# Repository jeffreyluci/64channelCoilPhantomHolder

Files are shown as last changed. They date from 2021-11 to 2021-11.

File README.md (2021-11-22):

# 64 Channel Coil Phantom Holder for FUNSTAR Phantom
Development resources for creating a [FUNSTAR](https://www.goldstandardphantoms.com/products/funstar/) phantom holder for a Siemens 64 channel Head/Neck coil

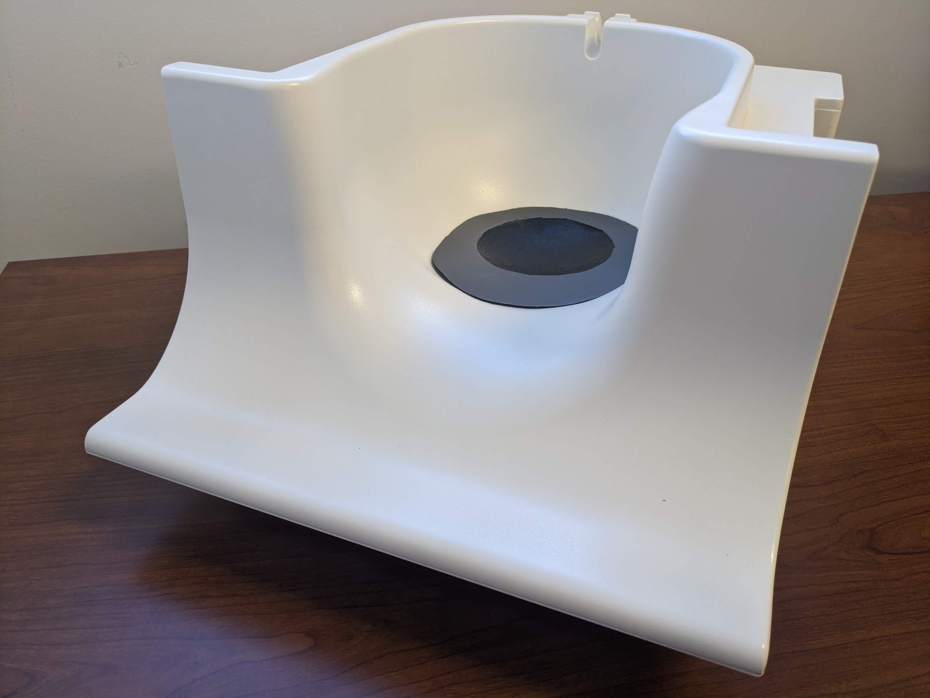
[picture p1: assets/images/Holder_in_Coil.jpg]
Phantom holder in Siemens 64 channel head coil


The analysis I perform for QA monitors individual coil elements, and the phantom's position in the coil affects loading and sensitivities of all the elements. Placing the phantom reproducibly within the coil housing enables more rigorous monitoring and comparison of long-term metrics. To that end, I have used CAD files of the coil housings to create my custom phantom holders. Unfortunately, having just moved to Rutgers University and switching to a Prisma, my primary coil for QA is now the 64 channel head/neck. Previously, I had used the 32 head. Snice I don't have, and didn't want to wait for the (approximately) 284 lawyers it takes to obtain the CAD files for this coil, I acquired a high resolution CT of the coil housing, and modeled the surface in [Autodesk Inventor.](https://www.autodesk.com/products/inventor/overview) From that, I created a holder that meshes with the surface of the coil, and has a shperoid cutout that matches the FUNSTAR outer diameter.

A few caveats. This phantom holder is in direct contact with the coil housing and does not provide any effective vibration mitigation measures. I am still trying to rigorously characterize the mechanical vibrations, and how much they affect the results of QA (if at all). I am also trying to get the CAD files for the 64 channel head/neck coil. If/when I am able to do that, I will create a revised version of this holder and update this posting.

I 3D printed the holder on an FDM printer using ABS as the filament material. My plan was to use this print as a prototype to see if my modeled coil surface needed any significant tweaks to resolve mismatched features. Once those tweaks were made, I would reprint the holder using a SLA or SLS printer. While placement of the center of the phantom ended up off center by about 2 mm, I was very pleased with the surface matching, and decided that I didn't need to improve upon the design or material.

The coil was printed with the flat surface down. That left the phantom mating depression quite rough from lack of enough supports. However, using a [Dremmel tool](https://us.dremel.com/en_US/products/-/show-product/tools/4300-high-performance-variable-speed-rotary-tool) on medium speed fitted with a [Dremel 414 polishing wheel](https://us.dremel.com/en_US/products/-/show-product/accessories/dremel-414-felt-polishing-wheel) cleaned it up very nicely. That process took only a few minutes. I recommend wearing a mask for this part of the process to prevent inhaling any ABS dust. I sure hope you can find a facemask somewhere. 

I coated the coil and phantom mating surfaces with (please don't laugh) [black Flex Seal spray.](https://flexsealproducts.com/products/flex-seal) (I figured if it's good enough to float a fishing boat . . .) I used 8 coats for the coil mating surface, and 5 coats for the phantom side. The rubberized surface provides excellent grip to prevent sliding, yet leaves no sticky residue or discoloration of the coil or phantom. I plan on peeling off the Flex Seal coating to reapply when/if it becomes brittle or loses its grippy properties. It peels off easily from the ABS, but it adheres strong enough that I'm not overly concerned about durability under normal use.

I have attached a zip file with photos of the holder after printing at various stages of finishing. I chose to mask off the flat surface of the holder, but if I had it to do over again, I wouldn't do that. It was unnecessary, and I probably reduced the lifetime of the rubber by creating "sharp" edges where the rubber could peel. The photos of the holder in the coil are a little misleading. The rubber intentionally curls up just a bit around the surface, and that makes it look as though there is a shadow indicating a gap between the holder and the coil surface. There isn't one. It's a very tight fit.

I have also attached STL files. One at "low" resolution for FDM printers, and one at "high" resolution for SLA or SLS printers. I used the FDM printer version, and its "smoothness" is more than adequate after rubberization. 

Finally, I have attached the AutoCAD Inventor model I created that subsequently produced the STL files. DM for my Venmo for gratuities!

I hope these help you, and if you have questions or need help using these resources, feel free to contact me. I'm always happy to help and collaborate.

## LICENSE and TERMS OF USE

All information contained in this repository is copyrighted by Jeffrey Luci, 2021. Jeffrey Luci grants non-exclusive, revocable license to use the information contained in this repository to all persons for non-commercial use, provided that works using information in this respository (including those that build upon, modify, or improve the design) in publication or presentation must reference this repository formally, in accordance with the accepted practices, procedures, and styles of the relevant publishing entity. **ALL** commercial use must be separately and individually licensed from Jeffrey Luci.

Jeffrey Luci reserves the right to modify, update, amend, append, expand, and revoke this and all subsequent licenses at any time and for any reason. Your use of any information held in this repository constitutes acceptance of these terms and the disclaimers that follow below.

## DISCLAIMERS

The information and technical files provided by Jeffrey Luci on this repository is for general informational purposes only. All information in the repository is provided in good faith, however I make no representation or warranty of any kind - express or implied - regarding the accuracy, adequacy, validity, reliability, availability, appropriateness, or completeness of any information in this repository.

Your access to and use of the information in this repository or any of its content is at your own risk. Jeffrey Luci is not responsible or liable for any damages arising or resulting from use of or inability to use the repository or any information contained in it, or from any action or decision taken as a result of using this repository.

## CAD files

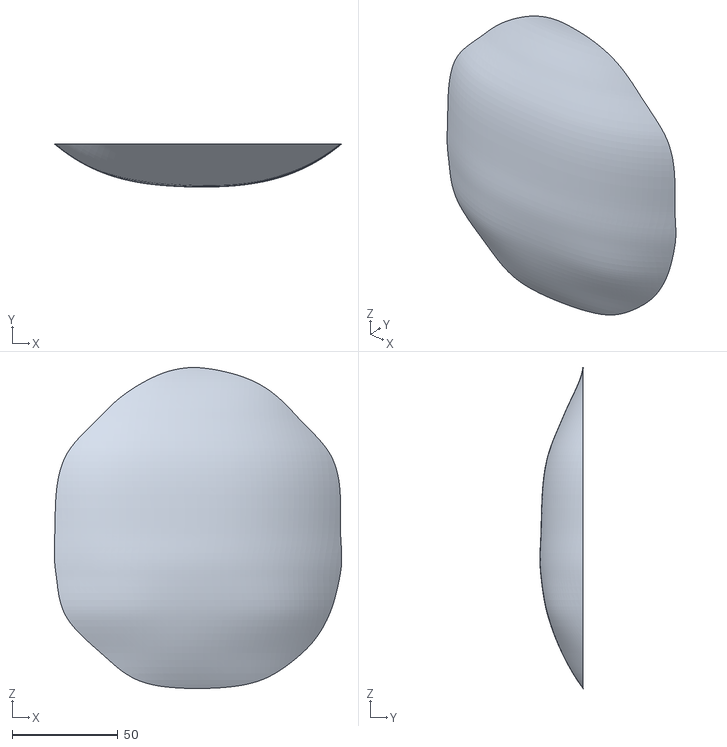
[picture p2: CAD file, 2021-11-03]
64 channel head coil phantom holder FDM.stl
136.1 x 20.4 x 152.0

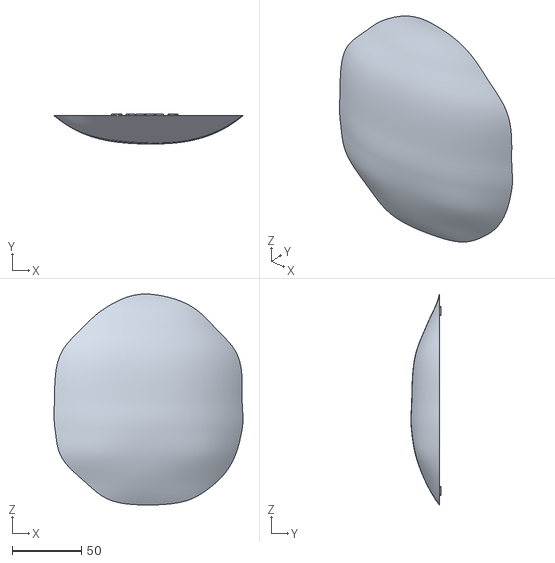
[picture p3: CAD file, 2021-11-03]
64 channel head coil phantom holder SLA.stl
136.1 x 21.7 x 152.0

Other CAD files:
64 channel head coil phantom holder.ipt
